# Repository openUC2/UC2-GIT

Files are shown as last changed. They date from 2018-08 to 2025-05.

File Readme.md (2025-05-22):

<p align="left">
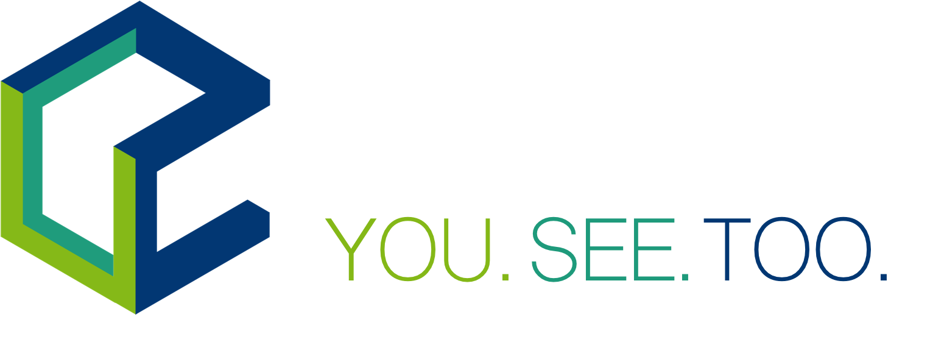
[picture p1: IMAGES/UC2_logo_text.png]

</p>

# **UC2 - Open and Modular Optical Toolbox**

**⚠️ IMPORTANT NOTICE:**
This repository is no longer actively maintained. But don’t worry—**openUC2 is more alive than ever!**
For the latest updates, documentation, and community discussions, please check out the following resources:

* 💬 **Forum**: [openuc2.discourse.group](https://openuc2.discourse.group)
* 📚 **Wiki**: [openuc2.github.io](https://openuc2.github.io)
* 🔧 **Firmware**: [youseetoo.github.io](https://youseetoo.github.io)
* 🌐 **Website**: [openuc2.com](https://openuc2.com)

**Open-source forever** – so we can become the *Raspberry Pi for optics!*

---

**New**: :mag_right: A [youtube seminar](https://www.youtube.com/watch?v=Jp5TOqvf7Nc&ab_channel=mitirtmfm) that describes UC2:  :mag:

**New**: :mag_right: The MiniBOX insert can be produced with a laser cutter now! Also, we improved the page and added some tips and trick for working with the [MiniBOX](./TheBOX/SimpleBOX)! Build it, use it, share your thoughts! :mag:

**New**: We got the official open hardware certification of OSHWA, under [`[OSHW] DE00110 | Certified open source hardware | oshwa.org/cert`](https://certification.oshwa.org/de000110.html)!

**New**: :boom: **UC2_v3 is now released!** :boom: [Watch how much time the IM cubes can save!](https://www.youtube.com/watch?v=M_oqieogAOo&feature=youtu.be&ab_channel=openUC2)   
*We are working on making the IM Cubes and Puzzles available for sale, but we are not able to offer a 'BUY' button yet. If you are interested in buying some components, contact us via email info@useetoo.org*

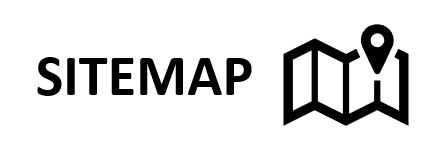
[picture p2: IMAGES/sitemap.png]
[](./SITEMAP.md)

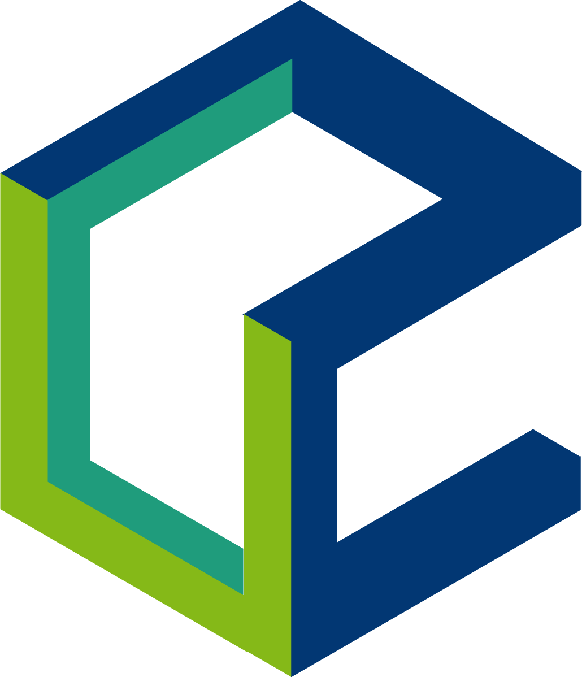
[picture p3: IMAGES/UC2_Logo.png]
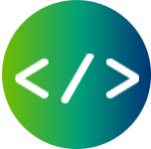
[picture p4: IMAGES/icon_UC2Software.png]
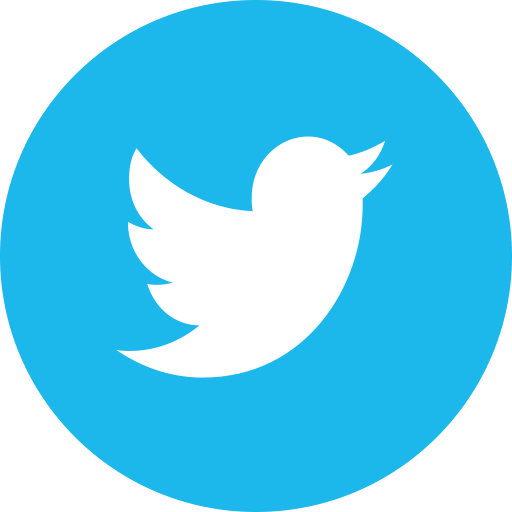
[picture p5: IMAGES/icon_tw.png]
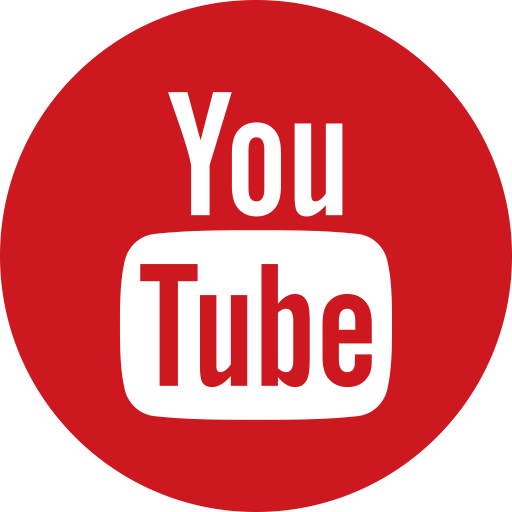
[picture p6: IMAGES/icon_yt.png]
[](https://www.useetoo.org) [](https://github.com/bionanoimaging/UC2-GIT) [](https://github.com/bionanoimaging/UC2-Software-GIT) [](https://twitter.com/openuc2)  [](https://www.youtube.com/channel/UCcHFzXTdC1Ro0OMnHS_54UA) 

Cite this repository: 

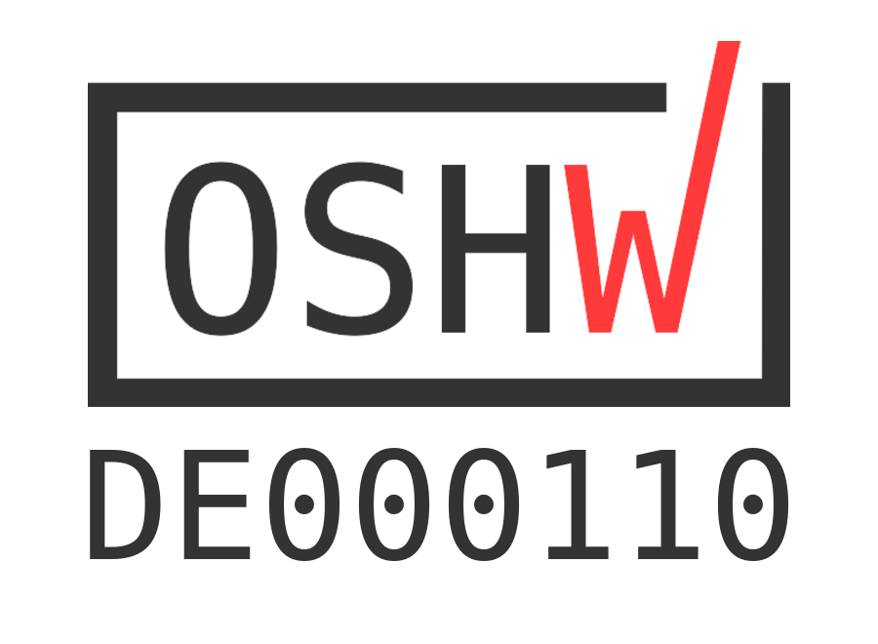
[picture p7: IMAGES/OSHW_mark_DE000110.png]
[](https://certification.oshwa.org/de000110.html)
This project provides certified open hardware.

---

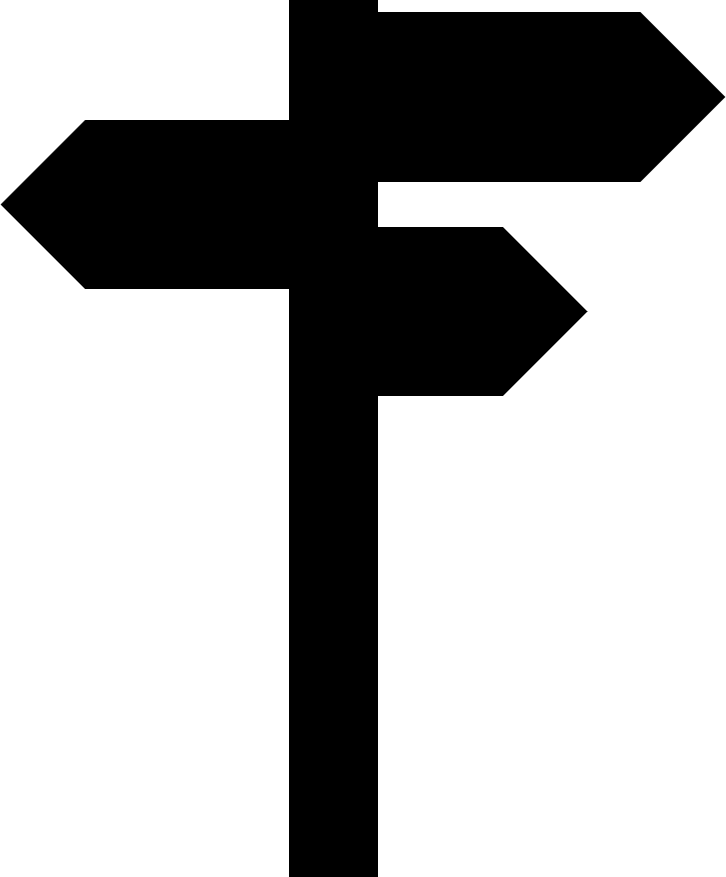
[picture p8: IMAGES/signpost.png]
#  Start here! Everything is open-source - simply join!

## Steps to reproduce and use the toolbox:
<p align="center">
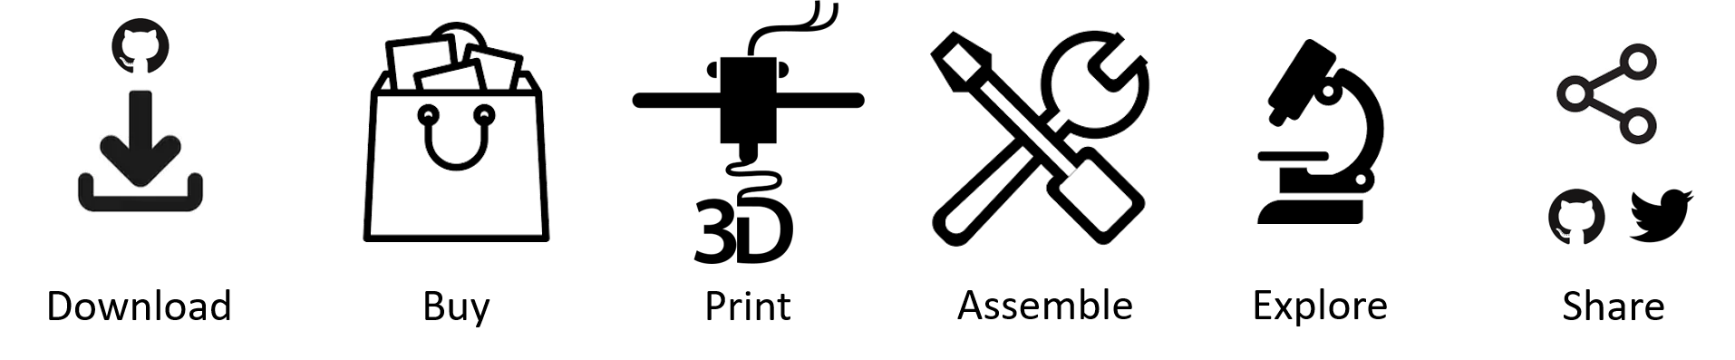
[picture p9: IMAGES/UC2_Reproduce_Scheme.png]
 
</p>

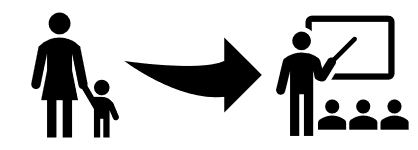
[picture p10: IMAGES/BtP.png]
## Too many new things? Follow our tutorials [ From a Beginner to a Professional](./TUTORIALS)!

## Already familiar? Click here if you are looking for...
TheBOX | General toolbox  | Specific setup |Workshops
:------:|:------:|:------:|:------:
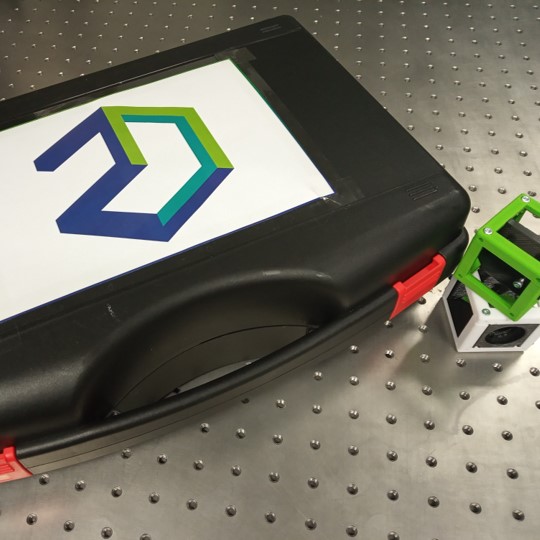
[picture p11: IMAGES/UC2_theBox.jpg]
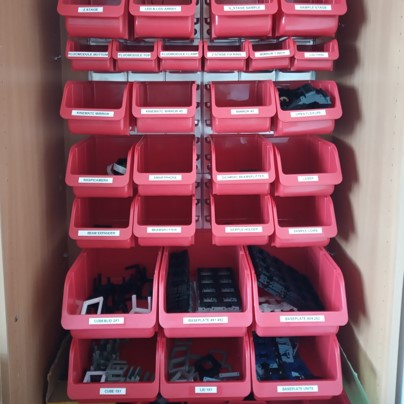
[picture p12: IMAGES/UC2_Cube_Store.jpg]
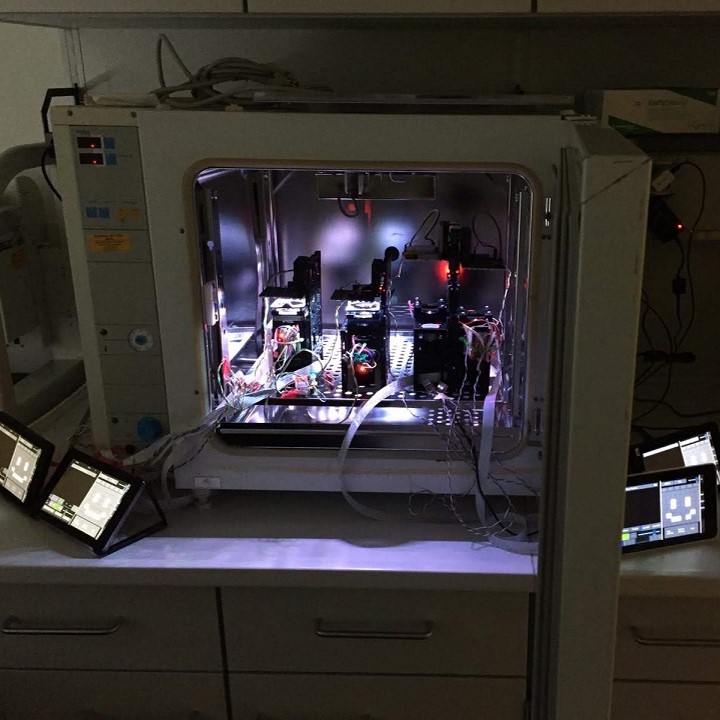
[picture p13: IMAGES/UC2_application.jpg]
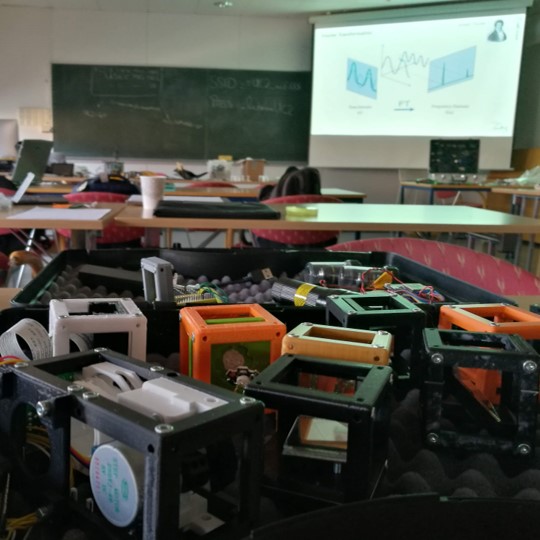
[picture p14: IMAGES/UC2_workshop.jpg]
[](./TheBOX)|[](./CAD)|[](./APPLICATIONS)|[](./WORKSHOP)
[Choose a version and build your own BOX.](./TheBOX) | [Explore the toolbox and its applications.](./CAD) | [Alternatives for many Microscopy methods... and more.](./APPLICATIONS) | [Host or join a UC2 workshop.](./WORKSHOP)

## [Get Involved! Contribute to the project!](CONTRIBUTING.md)

## ... or keep on reading to learn more!

---

## Making **open-science** great again!

**WARNING THIS SIDE IS UNDER REVISION! MANY CHANGES AHEAD!**

**UC2** is a general-purpose modular framework for making interactive (electro)-optical projects. Most optical systems such as microscopes follow a simple **4f** or Fourier-optical principle, where lenses are aligned such that focal-planes of adjacent components overlap to limit the amount of aberrations as much as possible and to be able to predict the system-behavior easily using Fourier-transforms.

<p align="center">
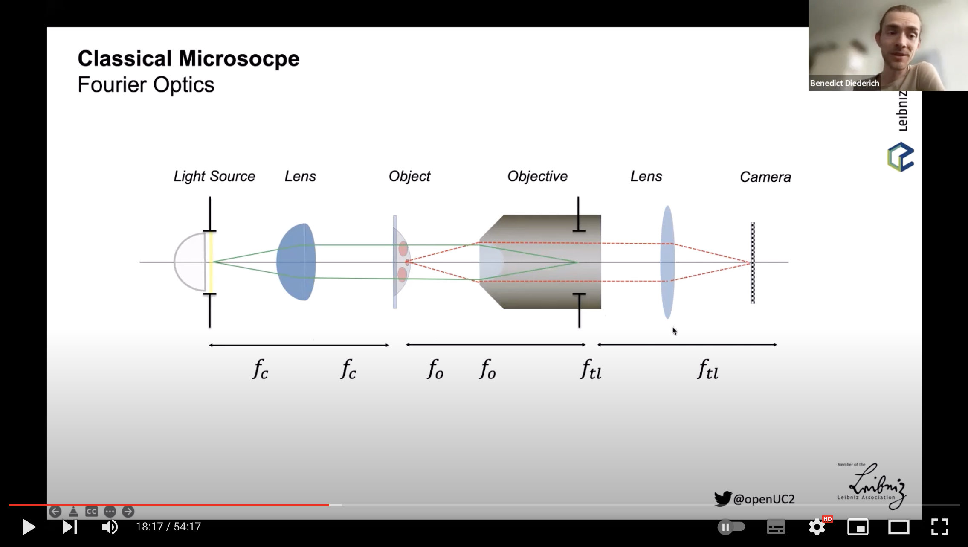
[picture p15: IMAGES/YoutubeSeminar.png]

<br> A recent seminar explaining the core concept of UC2 and their recent advances <br>
<p>

Following this idea, a microscope as shown in **Fig 1** creates an angular magnification depending on the focal lenghts of the objective f<sub>obj</sub> and tube lens f<sub>tube</sub>:

***M<sub>4f</sub>=  f<sub>tube</sub>/f<sub>obj</sub>***

<p align="center">
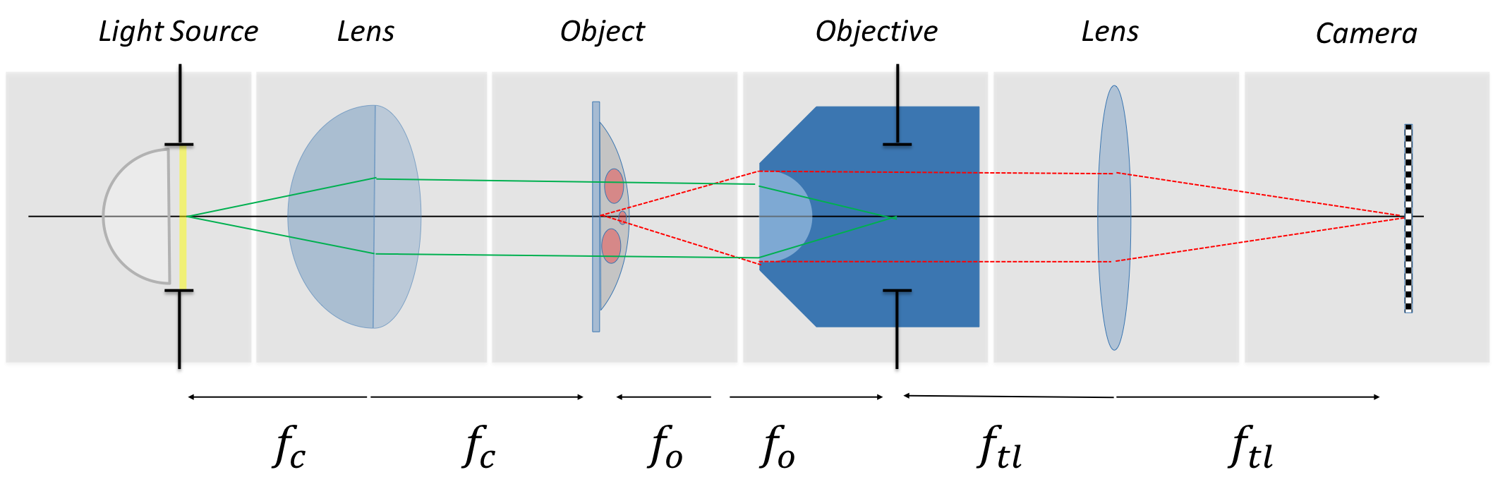
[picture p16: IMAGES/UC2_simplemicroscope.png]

<br> Fig. 1: Fourier-Optical Setup; Koehler Illumination where the illumination plane is conjugate to the objective pupil plane (BFP)
</p>

Besides optical components, the **UC2** building blocks can also host electronics such as **Arduinos** or **ESP32s** to create ''smart'' functions like LED array illumination, Z-stages, et cetera. Communication can be granted through the wired **USB Serial** BUS or the wireless **REST-API**. For this the dedicated [**UC2-REST**](https://github.com/openUC2/UC2-REST/blob/master/README.md) will help you setting everything up.

**UC2** is in active development. It is meant to be used not only by beginners, but also for professionals dealing with optical setups on a daily basis. Its magnetic click-and-go concept simplifies the process of aligning and adjusting the parts giving new tools acting as rapid-prototyping devices. It also comes with a series of open-source workshops (in the future) explaining the theory behind optics.

People are also encouraged to share their work. We are curious what the community is doing with our little blocks. All necessary details to modify the design of the blocks are given in the sub-folders of the specific folders. Share your ideas through our [@openUC2-Twitter account](https://twitter.com/openuc2).

With the version *UC2_v3* we introduced an **injection moulded (IM) cube**. This makes the assembly easier becuase no screws or magnets are needed for the Base Cube. But there is also a **3D-printed (3DP) cube** that is alternative to the IM one an it is fully compatible - the cubes and baseplates can be arbitrarily combined.   
Find out more about the two different Cube designs in [ASSEMBLY_CUBE_Base](./CAD/ASSEMBLY_CUBE_Base) and more about the baseplate puzzles in [ASSEMBLY_Baseplate](./CAD/ASSEMBLY_Baseplate).

*We are working on making the IM Cubes and Puzzles available for sale, but we are not able to offer a 'BUY' button yet. If you are interested in buying some components, contact us via email info@useetoo.org*

A full cube + base-plate looks like that:
<p align="center">
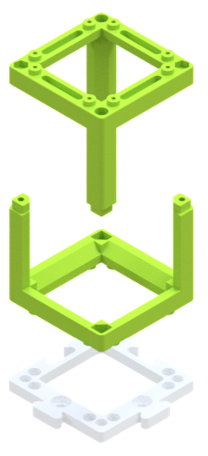
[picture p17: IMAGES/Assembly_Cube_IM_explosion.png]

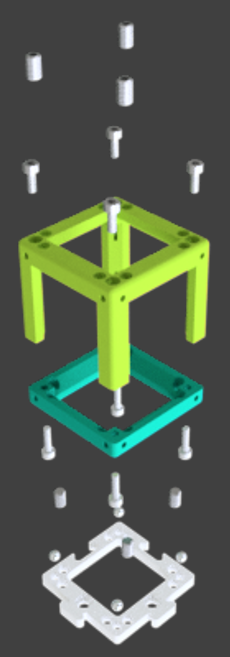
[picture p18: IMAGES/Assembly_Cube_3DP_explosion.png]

<br> Fig. 2: Assembly of the cube + base-plate; <br>
LEFT: IM Cube - Two identical halves of the Cube are pressed together, the Cube connects to the baseplate via lego-like pins; <br>
RIGHT: 3DP Cube - A set of ferro-magnetic screws hold the lid and base-cube in place and connect to four 5mm Neodym ballmagnets sitting in the baseplate, and extra set of M5 screws further fixes the cube to the baseplate and supports the alignment; Optical components find their place inside the cube.
</p>

:grey_exclamation: If you are still working with the v2 version of the cube, you find the documentation in the [UC2_v2 branch](https://github.com/bionanoimaging/UC2-GIT/tree/UC2_v2). Check out the Modular Developer Kit to learn about the [UC2 version history](./MDK#uc2-version-history).

**UC2** can be used with cameras from the Raspberry Pi world, but creates even more beautiful images with your cellphone. Thus making cutting edge-research not only affordable, but also available.
A more in-detail project description can be found in the [UC2 White-Paper](./TUTORIALS/DOCUMENTS/UC2_Whitepaper.pdf)

## UC2 as an "open-standard"

The idea is to use **UC2** as an open-standard or bridge to external hardware components and devices such as cameras or lenses. An already existing or customized adapter/insert creates the link to the **UC2** eco-system. A variety of ready-to-use adapters can be found in the folder [CAD](./CAD).

<p align="center">
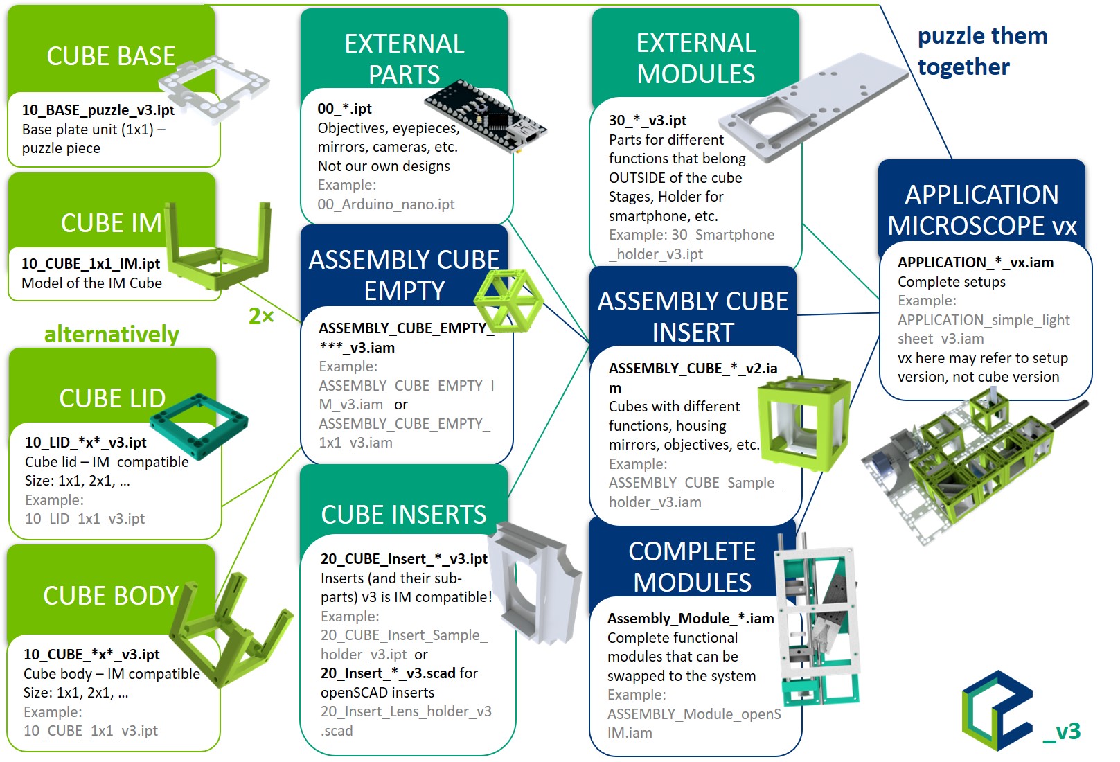
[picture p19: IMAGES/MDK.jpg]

<br> Fig. 3: The structure of any UC2 assembly follows the green lines; A basic cube can hold an insert thus adapting to different components (i.e. lenses, etc.); A number of assembled cube-modules can form a complex optical system here called application
</p>

A more in-detail description of the **MDK** (**M**odular **D**eveloper **K**it) which explains how ***your idea*** can be adapted to the module system can be found in the [MDK](./MDK)-folder. There you also found an explanation about the UC2 version history, if you found some confusing information through the repository.

If you have a new part, we are eager to see it. Please feel free to share it on available websites like Twitter, Thingiverse, Github or any other platform of choice!

### Read more about the project in our papers:
The UC2 paper: A versatile and customizable low-cost 3D-printed open standard for microscopic imaging is available on [Nature Communications](https://www.nature.com/articles/s41467-020-19447-9) 
All data from the paper is available in [Zenodo](https://doi.org/10.5281/zenodo.4018965)   
The Pre-print of the SIM+ISM paper is available on [Biorxiv](https://www.biorxiv.org/content/10.1101/2021.01.08.425840v1)    
The COSI conference paper is out on [OSA](https://www.osapublishing.org/abstract.cfm?uri=ISA-2019-ITh3B.5)  

Where next? [](./SITEMAP.md)

### Complete overview of setups, modules, parts to buy and parts to print
I'm afraid we outgrew the situation where we could provide a real complete overview. If you're looking for something specific, check the [SITEMAP](./SITEMAP.md) of the core repository and the [overview of the openUC2 repositories](./REPO_OVERVIEW.md).

For the basic modules and setups, find a complete shopping'n'printing list including estimated prices for all modules and setups in this [BILL OF MATERIALS](https://docs.google.com/spreadsheets/d/1U1MndGKRCs0LKE5W8VGreCv9DJbQVQv7O6kgLlB6ZmE/edit?usp=sharing)!

### List of available Setups

Our goal is to make as many setups as possible available, so that people can play with it. Basically everything's possible, you just need to think in blocks! Please have a look in the [APPLICATIONS](./APPLICATIONS/Readme.md) folder for the up to date list of the setups.

<p align="center">
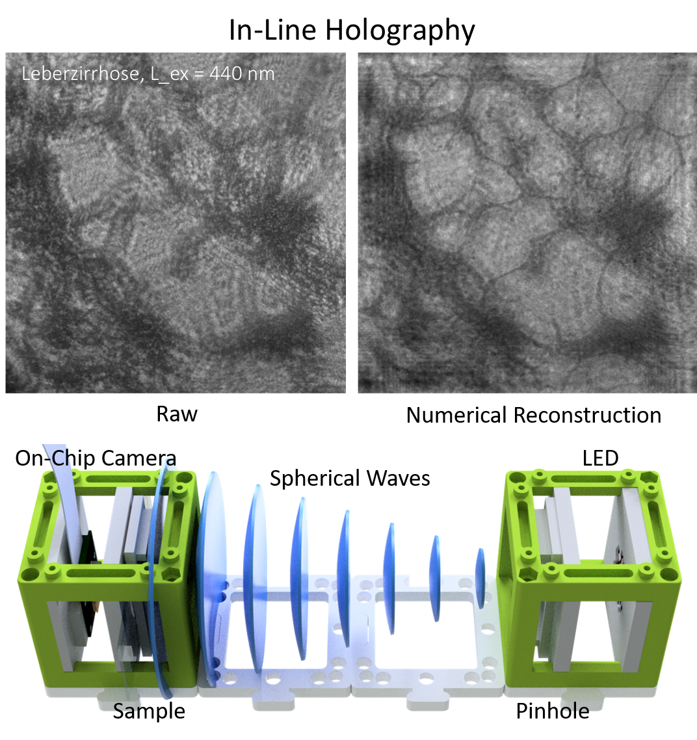
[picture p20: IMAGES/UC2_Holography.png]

<br> Fig. 4: In-line holographic microscope
</p>

### Repositories

Currently, **UC2** consists of the following repositories:

* [UC2 Hardware Repo (core)](https://github.com/openUC2/UC2-GIT) (this repository) - [SITEMAP](./SITEMAP.md)
* [UC2-REST Repo](https://github.com/openUC2/UC2-REST) - firmware for microcontrollers
* [UC2 ImSwitch](https://github.com/beniroquai/ImSwitch) - control software for microscopes
* A whole bunch of other repositories! In order to keep the main repository small and maintain a good structure, each sub-project has its own repository - find the [overview here](./REPO_OVERVIEW.md)

### Software

There is a GitHub repository dedicated for the UC2 software. It can be found in the [UC2-REST Repo](https://github.com/openUC2/UC2-REST). 

The old and deprecated Raspi version can be found [here](https://github.com/bionanoimaging/UC2-Software-GIT). This supports you with controller APPS for the Raspberry Pi and Android Cellphones.

### Workshops

The documented workshops can be found in the folder [WORKSHOP](./WORKSHOP) and give a step-by-step introduction into the system. We have done multiple workshops together with the HHMI Janelia Farm, UiO Oslo, Lichtwerkstatt Jena and Leibniz IPHT Jena e.V.  
If you're interested we are happy to host one near you!

## Get Involved

This project is open so that anyone can get involved. You don't even have to learn CAD designing or programming. Find ways you can contribute in  [CONTRIBUTING](CONTRIBUTING.md)

## Kits, License and Collaboration

<p >

</p>

This project is open-source and is released under the CERN open hardware license. Our aim is to make the kits commercially available.
We encourage everyone who is using our Toolbox to share their results and ideas, so that the Toolbox keeps improving. It should serve as a easy-to-use and easy-to-access general purpose building block solution for the area of STEAM education. All the design files are generally for free, but we would like to hear from you how is it going.

You're free to fork the project and enhance it. If you have any suggestions to improve it or add any additional functions make a pull-request or file an issue.

Please find the type of licenses [here](./License.md)

REMARK: All files have been designed using Autodesk Inventor 2019 (EDUCATION)

## Showcase

This is the mess you can end up during Fourier-optics session using UC2 components. Pure-fun! :-)

<p align="center">

</p>

## Credits
If you find this project useful, please like this repository, follow us on Twitter and cite the webpage! :-)

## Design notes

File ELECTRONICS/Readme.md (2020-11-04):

#  Electronics
 Here you'll find the schematics for the wiring of the UC2 parts.

* For printing and assembly of all the cubes and modules go to [CAD](../CAD)
* For complete setups go to [APPLICATIONS](../APPLICATIONS)
* For setups compilations go to [TheBOX](../TheBOX)
* For beginner's tutorials, how-to guides and more guidelines go to [TUTORIALS](../TUTORIALS)
* For information on the software go to the dedicated repository [UC2-Software-GIT](https://github.com/bionanoimaging/UC2-Software-GIT)
* For the Bill of Materials go to [RESOURCES](../TUTORIALS/RESOURCES)
* For anything else, have a look at the [SITEMAP](../SITEMAP.md)

---
# If all the wiring scares you, [click here ](./ELECTRONICS_FOR_DUMMIES)
---

Most connections can be established with pin-connection (male/female), as you see in the [simplified tutorial](./ELECTRONICS_FOR_DUMMIES). For durable connection, please solder everything! You're not expected to have perfect soldering skills though. Have a look in the [TUTORIALS](../TUTORIALS) for some soldering guidelines. Be careful not to mix up +/-, otherwise you might cause shortcuts which would very likely fry the Pi or the Arduinos/ESP32s.

## Available schemes and guidelines
* [Z-stage and Sample-Stage](./Z-Stage)
* [LED matrix](./LED-Matrix)
* [Fluo-LED for Z-stage](./FLUO-LED)
* [XY-Stage](./XY-Stage)
* [Raspberry Pi](./RASPBERRY-PI)
* [Magnetic connectors (v0)](./Magnetic-Connectors)

    This section needs an update!

## Wire Diagrams/Schematics
All schemes are put together with the Open-Source Software [Fritzing](http://fritzing.org/).

## General Wiring (Arduino Nano; I2C)
For the I2C Bus we use a 4-wire colour-code as follows:

- **5V** - White
- **GND** - Yellow
- **Data** - Green
- **CLK** - Brown

The junctions are connected with [WaGo Snapping Clamps, Compact Wago 2273-203 -> Amazon](https://www.amazon.de/Wago-VERBINDUNGSKLEMME-3POL-2273-203/dp/B075ZRQCGZ):
<p align="center">
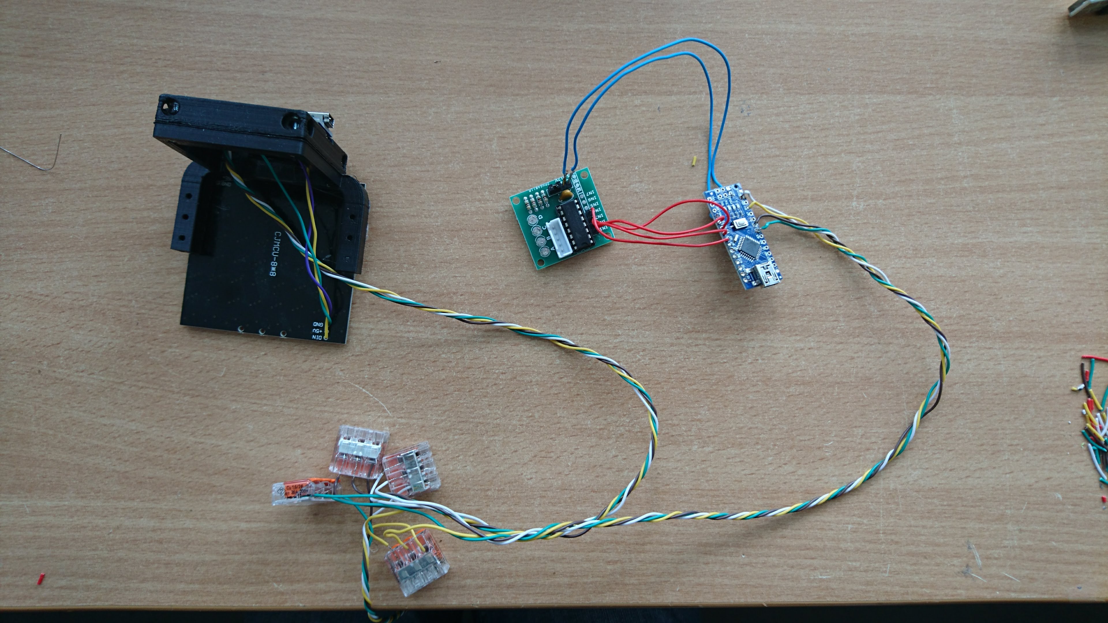
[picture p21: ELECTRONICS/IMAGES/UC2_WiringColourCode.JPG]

</p>

# Done with the wiring? Then it's time for [software](https://github.com/bionanoimaging/UC2-Software-GIT)!

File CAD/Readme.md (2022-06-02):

## CAD Files
 Here you can find the necessary .stl parts for the different modules (cubes) and setups ([APPs](../APPLICATIONS)).

* For complete setups go to [APPLICATIONS](../APPLICATIONS)
* For setups compilations go to [TheBOX](../TheBOX)
* For beginner's tutorials, how-to guides and more guidelines go to [TUTORIALS](../TUTORIALS)
* For information on the electronic parts go to [ELECTRONICS](../ELECTRONICS)
* For information on the software go to the dedicated repository [UC2-Software-GIT](https://github.com/bionanoimaging/UC2-Software-GIT)
* For the Bill of Materials go to [RESOURCES](../TUTORIALS/RESOURCES)
* For anything else, have a look at the [SITEMAP](../SITEMAP.md)

This is a growing list of available modules coming along with tutorials and assembly instructions. The most important part is the core building block as you find in every modular toolbox. A detailed description of the **UC2** cube can be found [here](./ASSEMBLY_CUBE_Base_v2/Readme.md).

## General Naming Convention and Structure of UC2

<p align=center>

</p>

## UC2 version history
When you search through the repository, you find that not all the images show the same cubes and baseplates. This is due to the evolution of the basic building blocks. In order to help you not to get lost, in the [Modular Developer Kit](../MDK#uc2-version-history) is a short explanation of how the cubes evolved.

#### v3 = 3D-printed AND Injection Moulded (*November 2020*)
This is the current version. The cube comes in two versions that are fully compatible with each other. You can either print all the baseplates and cubes and assemble and connect them using screws and magnets, or you can use the IM cubes and baseplate puzzles that connect via the lego-like pins.

The IM cube is shown on the left, the 3DP (3D-printed) cube is on the right. Find the details about the base cube in [ASSEMBLY_CUBE_Base](./ASSEMBLY_CUBE_Base).
<p align=center>
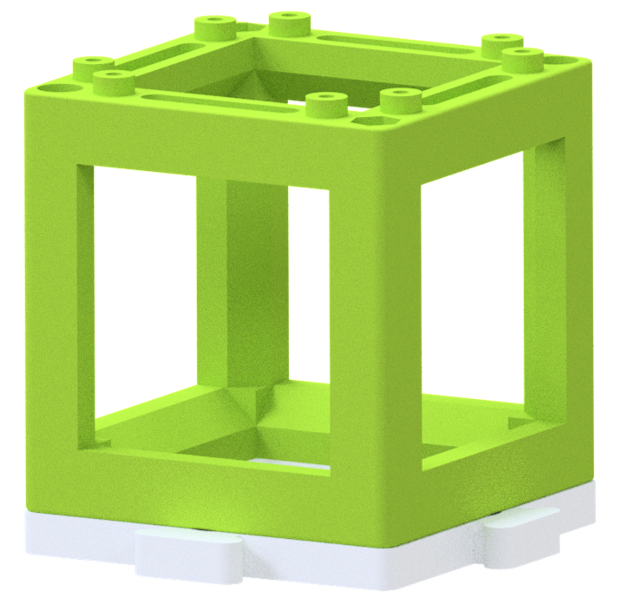
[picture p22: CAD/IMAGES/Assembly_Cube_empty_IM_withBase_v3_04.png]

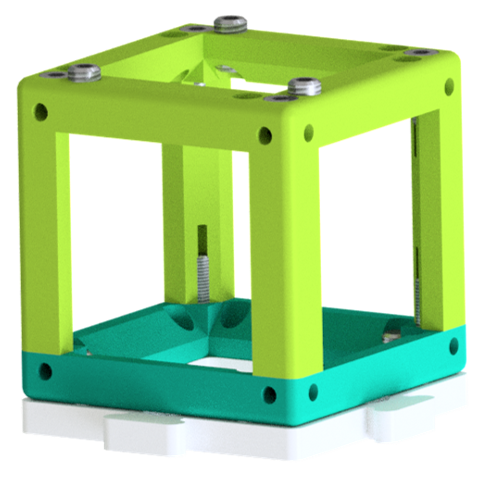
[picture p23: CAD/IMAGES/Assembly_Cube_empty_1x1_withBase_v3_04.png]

</p>

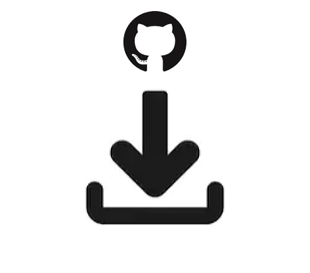
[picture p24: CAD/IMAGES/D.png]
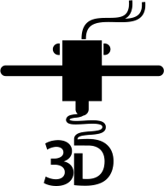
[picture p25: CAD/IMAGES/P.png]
##  Printing
The .stl files of the respective modules can be downloaded and printed. Have a look at our [TUTORIALS](../TUTORIALS) section for some introductory information regarding 3D printing, shopping for components and more.

## List of available Modules (CUBEs):
Each folder contains a step-by-step tutorial which describes how the module has to be assembled.

Link             |  Image of the part
:-------------------------:|:-------------------------:
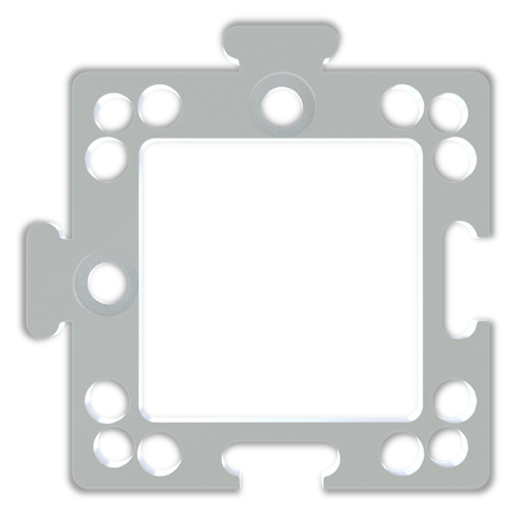
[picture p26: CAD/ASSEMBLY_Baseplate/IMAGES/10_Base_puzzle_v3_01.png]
[Base Plate puzzle](./ASSEMBLY_Baseplate)  |  [](./ASSEMBLY_Baseplate)
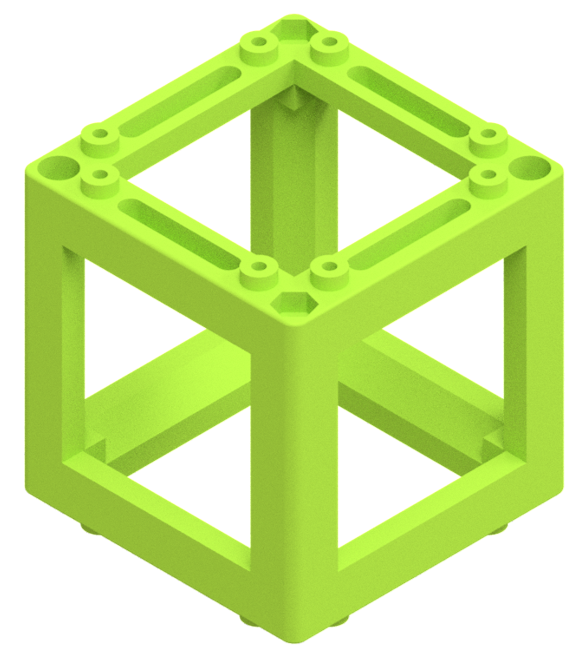
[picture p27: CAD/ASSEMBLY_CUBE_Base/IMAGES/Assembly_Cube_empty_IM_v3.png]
[CUBE Base](./ASSEMBLY_CUBE_Base)  |  [](./ASSEMBLY_CUBE_Base)
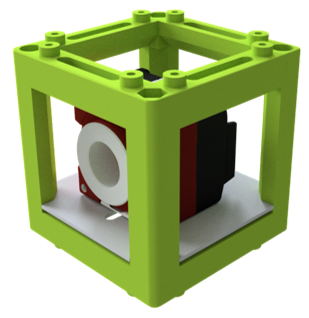
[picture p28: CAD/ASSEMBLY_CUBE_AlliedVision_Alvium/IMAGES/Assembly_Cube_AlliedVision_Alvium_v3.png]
[Allied Vision Cam](./ASSEMBLY_CUBE_AlliedVision_Alvium) | [](./ASSEMBLY_CUBE_AlliedVision_Alvium)
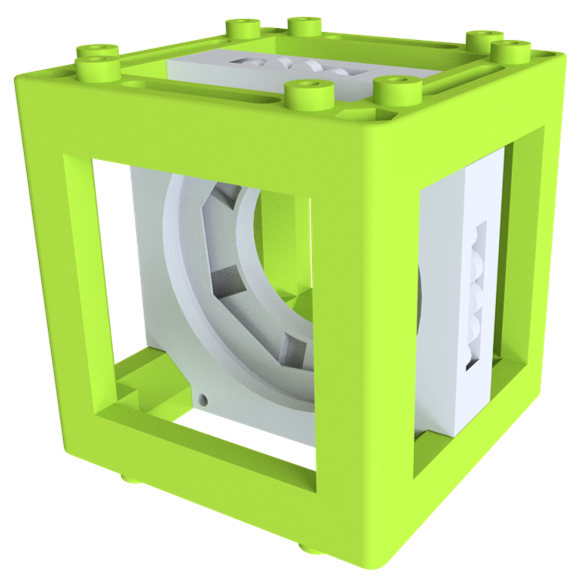
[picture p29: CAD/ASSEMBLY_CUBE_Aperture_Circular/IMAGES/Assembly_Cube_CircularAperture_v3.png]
[Circular Aperture](./ASSEMBLY_CUBE_Aperture_Circular)  |  [](./ASSEMBLY_CUBE_Aperture_Circular)
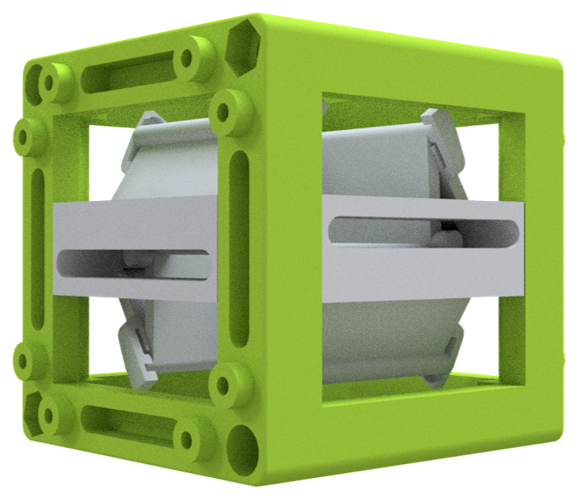
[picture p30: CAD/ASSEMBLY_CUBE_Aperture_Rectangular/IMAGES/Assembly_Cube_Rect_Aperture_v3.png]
[Rectangular Aperture](./ASSEMBLY_CUBE_Aperture_Rectangular)  |  [](./ASSEMBLY_CUBE_Aperture_Rectangular)
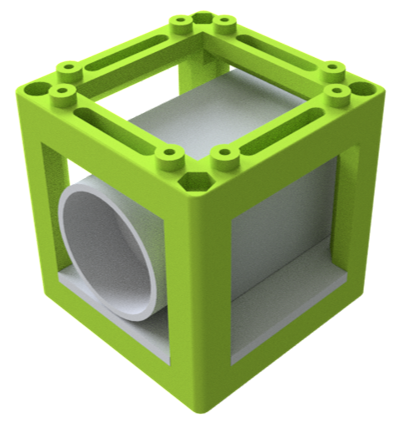
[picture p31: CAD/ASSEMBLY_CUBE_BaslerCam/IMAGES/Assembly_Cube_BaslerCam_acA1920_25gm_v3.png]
[Basler Cam](./ASSEMBLY_CUBE_BaslerCam) | [](./ASSEMBLY_CUBE_BaslerCam)
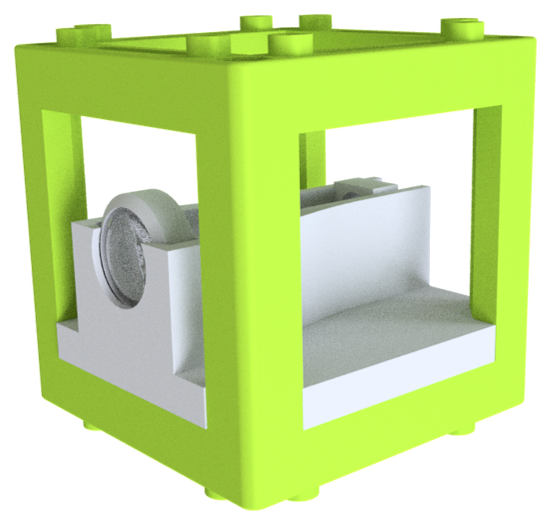
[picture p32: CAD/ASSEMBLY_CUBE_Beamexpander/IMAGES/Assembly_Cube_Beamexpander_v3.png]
[Beam Expander](./ASSEMBLY_CUBE_Beamexpander)  |  [](./ASSEMBLY_CUBE_Beamexpander)
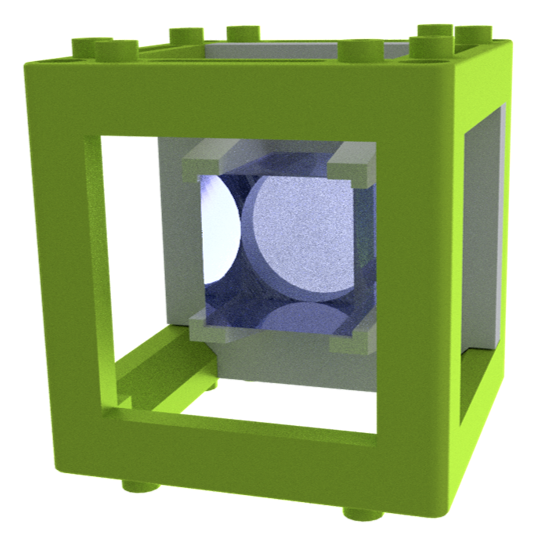
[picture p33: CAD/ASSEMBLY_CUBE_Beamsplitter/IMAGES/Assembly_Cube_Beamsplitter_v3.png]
[Beam splitter](./ASSEMBLY_CUBE_Beamsplitter)  |  [](./ASSEMBLY_CUBE_Beamsplitter)
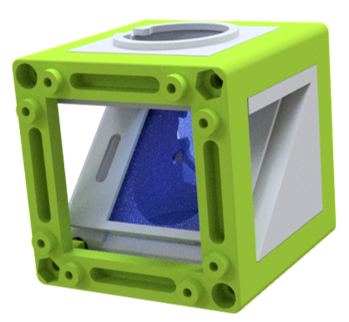
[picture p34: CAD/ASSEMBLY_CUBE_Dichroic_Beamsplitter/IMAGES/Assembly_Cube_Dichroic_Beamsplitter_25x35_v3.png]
[Dichroic Beam splitter](./ASSEMBLY_CUBE_Dichroic_Beamsplitter) | [](./ASSEMBLY_CUBE_Dichroic_Beamsplitter)
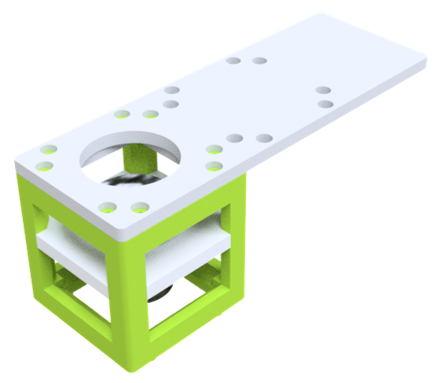
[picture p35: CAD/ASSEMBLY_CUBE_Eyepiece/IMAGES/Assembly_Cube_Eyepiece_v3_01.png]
[Eyepiece + Smartphone](./ASSEMBLY_CUBE_Eyepiece) | [](./ASSEMBLY_CUBE_Eyepiece)
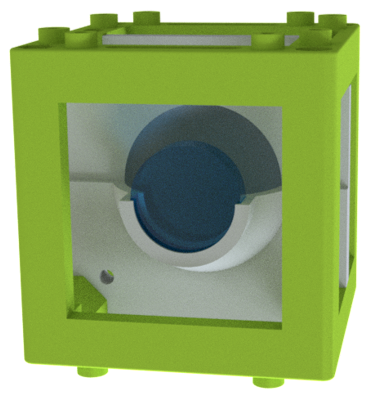
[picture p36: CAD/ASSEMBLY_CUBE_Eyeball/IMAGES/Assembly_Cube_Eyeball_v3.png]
[Eyeball Cube ](./ASSEMBLY_CUBE_Eyeball) | [](./ASSEMBLY_CUBE_Eyeball)
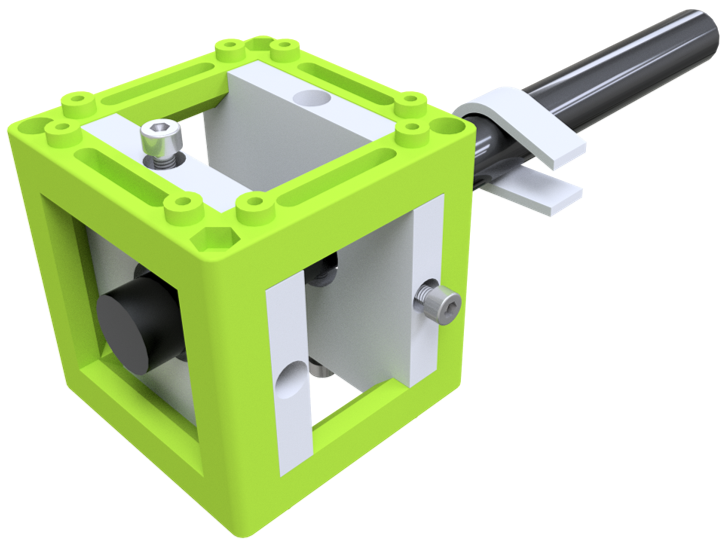
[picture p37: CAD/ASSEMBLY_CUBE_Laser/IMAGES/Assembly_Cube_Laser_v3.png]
[Laser](./ASSEMBLY_CUBE_Laser) | [](./ASSEMBLY_CUBE_Laser)
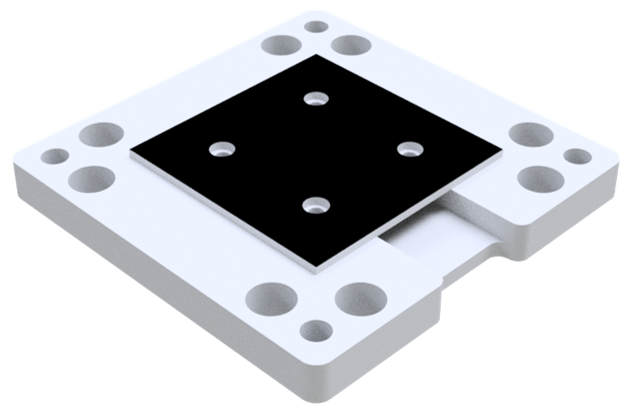
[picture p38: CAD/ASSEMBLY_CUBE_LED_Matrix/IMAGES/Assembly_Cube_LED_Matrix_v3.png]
[LED Matrix](./ASSEMBLY_CUBE_LED_Matrix) | [](./ASSEMBLY_CUBE_LED_Matrix)
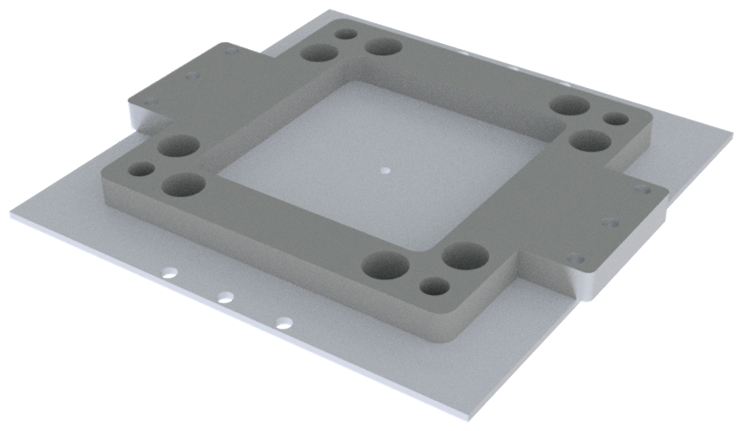
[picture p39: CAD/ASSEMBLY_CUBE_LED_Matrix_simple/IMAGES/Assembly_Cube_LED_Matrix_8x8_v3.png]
[LED Matrix (simple)](./ASSEMBLY_CUBE_LED_Matrix_simple) | [](./ASSEMBLY_CUBE_LED_Matrix_simple)
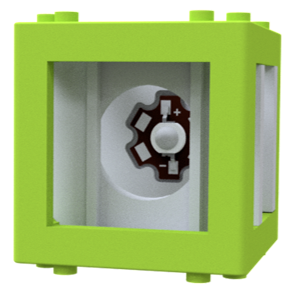
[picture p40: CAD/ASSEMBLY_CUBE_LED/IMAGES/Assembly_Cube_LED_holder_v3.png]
[LED Star](./ASSEMBLY_CUBE_LED) | [](./ASSEMBLY_CUBE_LED)
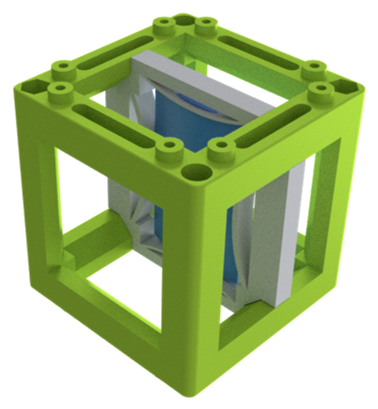
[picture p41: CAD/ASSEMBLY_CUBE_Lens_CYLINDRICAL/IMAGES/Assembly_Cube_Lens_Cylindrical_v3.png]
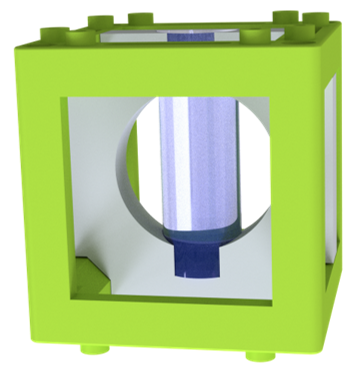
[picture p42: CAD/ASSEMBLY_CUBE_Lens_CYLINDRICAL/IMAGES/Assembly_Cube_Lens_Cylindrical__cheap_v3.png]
[Lens (cylindrical)](./ASSEMBLY_CUBE_Lens_CYLINDRICAL) | [](./ASSEMBLY_CUBE_Lens_CYLINDRICAL)
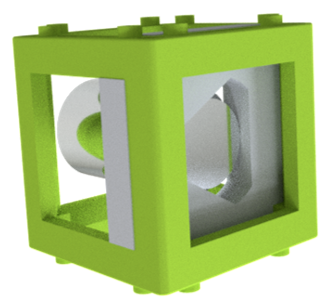
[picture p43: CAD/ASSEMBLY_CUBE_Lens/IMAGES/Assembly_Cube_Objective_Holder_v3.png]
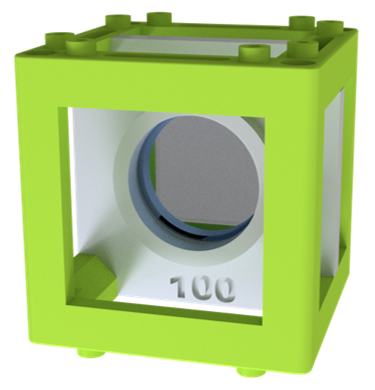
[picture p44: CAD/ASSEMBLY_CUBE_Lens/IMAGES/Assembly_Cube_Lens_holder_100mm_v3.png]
[Lens (standard)](./ASSEMBLY_CUBE_Lens) | [](./ASSEMBLY_CUBE_Lens)
[Mirror (45°)](./ASSEMBLY_CUBE_Mirror_45) | [](./ASSEMBLY_CUBE_Mirror_45) [](./ASSEMBLY_CUBE_Mirror_45)
[Mirror, kinematic (45°)](./ASSEMBLY_CUBE_Mirror_Kinematic_45) | [](./ASSEMBLY_CUBE_Mirror_Kinematic_45)
[Mirror, kinematic (0°)](./ASSEMBLY_CUBE_Mirror_Kinematic) | [](./ASSEMBLY_CUBE_Mirror_Kinematic)
[Raspi Cam](./ASSEMBLY_CUBE_RaspiCam) | [](./ASSEMBLY_CUBE_RaspiCam)
[S-Stage v2.1](./ASSEMBLY_CUBE_S-STAGE_v2.1) | [](./ASSEMBLY_CUBE_S-STAGE_v2.1)
[Sample Holder Cube](./ASSEMBLY_CUBE_Sample_Holder) | [](./ASSEMBLY_CUBE_Sample_Holder)
[Magnetic Sample Holder](./ASSEMBLY_CUBE_Sample_Holder) | [](./ASSEMBLY_CUBE_Sample_Holder)
[Sample Holder Comb](./ASSEMBLY_CUBE_Sample_Holder) | [](./ASSEMBLY_CUBE_Sample_Holder)
[Thorlabs Adapter](./ASSEMBLY_CUBE_Thorlabs) | [](./ASSEMBLY_CUBE_Thorlabs)
[Z-Stage (Objective) mechanical](./ASSEMBLY_CUBE_Z-STAGE_mechanical) | [](./ASSEMBLY_CUBE_Z-STAGE_mechanical)
[Z-Stage (Sample) v3](./ASSEMBLY_CUBE_Z-STAGE_sample) | [](./ASSEMBLY_CUBE_Z-STAGE_sample)
[XYZ-Stage v0](./ASSEMBLY_XYZ-STAGE_v0) | [](./ASSEMBLY_XYZ-STAGE_v0)
[ASSEMBLY_CUBE_ArduCamUSB](./ASSEMBLY_CUBE_ArduCamUSB) | [](./ASSEMBLY_CUBE_ArduCamUSB)

## More external modules 
Link             |  Image of the part
:-------------------------:|:-------------------------:
[Optics rotator (e.g. Diffuser, Polarizer)](https://github.com/openUC2/UC2-Motorized-Rotator) | [](https://github.com/openUC2/UC2-Motorized-Rotator)
[Microsyringepump](https://github.com/openUC2/UC2-MicroSyringePump) | [](https://github.com/openUC2/UC2-MicroSyringePump)
[Multicolour Module](https://github.com/openUC2/UC2-MultiColour) | [](https://github.com/openUC2/UC2-MultiColour)
[Waveguide Coupling Module](https://github.com/openUC2/UC2-waveguiding) | [](https://github.com/openUC2/UC2-waveguiding)
[Motorized XY table](https://github.com/openUC2/UC2-Motorized-XY-Table) | [](https://github.com/openUC2/UC2-Motorized-XY-Table)
[Micromanipulator Module](https://github.com/openUC2/openCM2_hardware) | [](https://github.com/openUC2/openCM2_hardware)
[Motorized XY micrometer stage](https://github.com/openUC2/UC2-MicronStage) | [](https://github.com/openUC2/UC2-MicronStage)

## List of available Supplements:
* [ELECTRONICS-RaspiTFT-Case](./EXT_ELECTRONICS-RaspiTFT-Case)
* [ELECTRONICS-Mount](./EXT_ELECTRONICS-Mount)
* [Alignment tool](./EXT_Alignment_Tool)
* [Adapter to openflexure stage](./CUBE_INSERT_OpenFlexure_Deltastage)

##  List of available [Applications (APPs)](../APPLICATIONS)

### Complete overview of setups, modules, parts to buy and parts to print
Find a complete shopping'n'printing list including estimated prices for all modules and setups in this [GoogleDrive Spreadsheet](https://docs.google.com/spreadsheets/d/1U1MndGKRCs0LKE5W8VGreCv9DJbQVQv7O6kgLlB6ZmE/edit?usp=sharing)!

##  Participate
If you have a cool idea, please don't hesitate to contact us, we are happy to incorporate it in our design to make it even better.  
More setups are coming soon!
Inspire us with your ideas - we try to make it work! :-)

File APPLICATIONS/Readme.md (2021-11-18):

## Applications
 Here you can find all the optical setups we tested or proposed so far.

* For printing and assembly of all the cubes and modules go to [CAD](../CAD)
* For setups compilations go to [TheBOX](../TheBOX)
* For beginner's tutorials, how-to guides and more guidelines go to [TUTORIALS](../TUTORIALS)
* For information on the electronic parts go to [ELECTRONICS](../ELECTRONICS)
* For information on the software go to the dedicated repository [UC2-Software-GIT](https://github.com/bionanoimaging/UC2-Software-GIT)
* For the Bill of Materials go to [RESOURCES](../TUTORIALS/RESOURCES)
* For anything else, have a look at the [SITEMAP](../SITEMAP.md)

This is a growing list of available optical setups coming along with tutorials and alignment instructions. The most important part is the core building block as you find in every modular toolbox. A detailed description of the the **UC2** cube can be found [here](../CAD/ASSEMBLY_CUBE_Base_v2/Readme.md).

##  List of available Applications (APPs)

### Compilations

* [TheBOX: Concept of a ready-to-use box containing multiple setups at once](../TheBOX/)
* [SimpleBOX: Optical setups from elementary to high-school level ](../TheBOX/SimpleBOX)
* [FullBOX: Optical setups from high-school to university level (contains electronics)](../TheBOX/FullBOX)
* [CourseBOX: Optical setups for Optics and Microscopy courses](../TheBOX/CourseBOX)
* [PolarBOX : Optical setups for the polarization of light ](../TheBOX/PolarBOX)

### SIMPLE Setups
* [SIMPLE - Projector](./APP_SIMPLE-Projector)
* [SIMPLE - Telescope](./APP_SIMPLE-Telescope)
* [SIMPLE - Smartphone Microscope](./APP_SIMPLE-Smartphone_Microscope)

### BASIC Setups
* [In-Incubator Microscope with X/Y/Z-control and adaptive illumination](./APP_Incubator_Microscope)
* [Light sheet Microscope](./APP_LIGHTSHEET_Workshop)
* [In-line Holographic Microscope](./APP_INLINE_HOLOGRAM)
* [Abbe Diffraction Experiment](./APP_Abbe_Setup)
* [Michelson Interferometer (Interference effect of light)](./APP_Michelson_Interferometer)
* [Mach-Zehnder Interferometer (Interference effect of light)](./APP_Mach-Zehnder_Interferometer)
* [Double Slit Experiment (Interference effect of light)](./APP_Double-slit_Experiment)
* [Spectrometer](APP_Spectrometer)

### POLARIZATION Setups
* [Crossed Polarizers](APP_POL_Crossed_Polarizers)
* [Three Polarizers](APP_POL_Three_Polarizers)
* [Circular Polarizer](APP_POL_Circular_Polarizer)
* [Optically Active Solution Experiment](APP_POL_Polarization_using_optically_active_solution)
* [Brewster's Angle Experiment](APP_POL_Brewster_Angle_Experiment)
* [Stress Birefringence](APP_POL_Stress_Birefringence)
* [Many Microscope Slides Experiment](APP_POL_Many_Microscope_Slides_Experiment)
* [Newton's Rings Experiment](APP_POL_Newtons_Rings_Experiment)

### COMPLEX Setups and sub-projects
All the more complicated systems have their own repository - see the overview [here](../REPO_OVERVIEW.md).

## General Naming Convention and Structure of UC2

<p align=center>

</p>

## UC2 version history
When you search through the repository, you find that not all the images show the same cubes and baseplates. This is due to the evolution of the basic building blocks. In order to help you not to get lost, in the [Modular Developer Kit](../MDK#uc2-version-history) is a short explanation of how the cubes evolved.

#### v3 = 3D-printed AND Injection Moulded (*November 2020*)
This is the current version. The cube comes in two versions that are fully compatible with each other. You can either print all the baseplates and cubes and assemble and connect them using screws and magnets, or you can use the IM cubes and baseplate puzzles that connect via the lego-like pins.

The IM cube is shown on the left, the 3DP (3D-printed) cube is on the right. Find the details about the base cube in [ASSEMBLY_CUBE_Base](../CAD/ASSEMBLY_CUBE_Base).
<p align=center>


</p>

##  List of available Modules (CUBEs):
A list of available Cubes that are the building blocks of all our setups can be found in [CAD](../CAD).

### Complete overview of setups, modules, parts to buy and parts to print
Find a complete shopping'n'printing list including estimated prices for all modules and setups in this [GoogleDrive Spreadsheet](https://docs.google.com/spreadsheets/d/1U1MndGKRCs0LKE5W8VGreCv9DJbQVQv7O6kgLlB6ZmE/edit?usp=sharing)!

##  Participate
If you have a cool idea, please don't hesitate to contact us, we are happy to incorporate it in our design to make it even better.  
More setups are coming soon!
Inspire us with your ideas - we try to make it work! :-)

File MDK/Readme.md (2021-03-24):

# Modular Devoloper Kit - MDK

V3 – 30.11.2020 Benedict Diederich, Barbora Marsikova

If you want to adapt your ideas to the ***UC2*** framework this document provides you with all the necessary information. We provide a detailed description of the definitions, versions, intentions and files. Once you have introduced your idea into the system, please share it so that others can benefit from it!

The CAD templates can be found in the [CAD](./CAD)-folder.

All the original design files as well as all the STL files can be found is [CAD/RAW](../CAD/RAW).

### Definitions

The UC2 framework requires the introduction of several new concepts. These terms are defined in the table below and illustrated in a series of figures.

The Names can be found in the chart below (Fig 1). The chart also represents the logical structure of building a setup using UC2 elements.

The scheme describes the structure in which the toolbox is designed, therefore its explaining the naming convention of the design files (Inventor, openSCAD). There are a few differences between that and the repository CAD folder - those are noted in the table below.

<p align=center>

<br> <em>Fig. 1: Modular Developer Kit chart</em>
</p>

Name | Description
:---:|:---:
**CUBE (Baseplate)** | The **BASE puzzle pieces**, the basic units, are joined into the **BASEPLATE** (“skeleton” of the setups). The Baseplate can have any shape any size, depending on how many puzzles you use and how you put them together. It allows you to build setups in three dimensions when you 'sandwich' the layers of cubes and baseplates. This is the frame and backplane of the UC2 project, determining the size and layout of the optical system. 3D-printed UC2 modules attach to the square baseplate positions using ball-magnets and ferro-magnetic screws. The injection moulded cubes attach via their lego-like pins. Find the details of the baseplates on their [CAD page](../CAD/ASSEMBLY_Baseplate). *(Git: ASSEMBLY_Baseplate)*
**CUBE (IM)** | The injection moulded (IM) is a half of the cube. The **ASSEMBLY CUBE (empty)** cube is composed of these two identical halves and can be easily assembled by their press-fit mechanism. The assembled IM cube has two sides with eight lego-like pins each to attach to the baseplate. *(Git: ASSEMBLY_CUBE_BASE)*
**CUBE (Body)** | Alternatively, the whole cube can also be 3D-printed. Then the **ASSEMBLY CUBE (empty)** consist of the body- and the lid-part which get screwed together. Screws can be inserted on all sides in order to build setups in three dimensions.
**CUBE (Lid)** | The lid closes the 3D-printed cube when attached by screw to the body. It can carry electronics like microcontrollers (e.g. Arduino, ESP32). By adding wires to the screws closing the lid electronic components can be supplied with electrical power.
**ASSEMBLY CUBE (empty)** | The raw cube - the basic building block comes in two versions: 3D-printed and injection moulded. Both of them have the same dimensions and symmetry, so the insert fit them all. The similarities and differences of the two systems are explained under this table in the *UC2 version history section*. Note that the MDK only details the specification of the Cube and Base to the extent that it is necessary for module developers to develop modules. Find the details of the Cube on its [CAD page](../CAD/ASSEMBLY_CUBE_Base). *(Git: ASSEMBLY_CUBE_BASE)*
**CUBE INSERTS** | Cube Inserts are physical components that implement various functions into the system by adapting **EXTERNAL PARTS** to the **ASSEMBLY CUBE INSERT**. They fit the inner dimensions of the cube. There are two types of inserts: perpendicular (to the optical axis) and diagonal. They serve as holders for various components like  lenses, mirrors, cameras, filters, and other components demanded by the application. Existing inserts can be adjusted to fit specific parts (i.e. lens diameters).
**EXTERNAL PARTS** | Everything which is not part of the UC2-system or can not be 3D printed is termed as an EXTERNAL PART. This can be commercially available parts like objectives, lenses, LEDs, etc., but also 3D-printed parts from other projects (e.g. openflexure stage).
**ASSEMBLY CUBE (insert)** | This is the combination of the ASSEMBLY CUBE (empty) and a CUBE INSERTS. Since the ASSEMBLY CUBEs are the building blocks of a UC2 setup, adding features is accomplished by hardware plugins also called CUBE INSERTS.
**EXTERNAL MODULES** | Using EXTERNAL MODULES one adapt EXTERNAL PARTS that typically do not fit inside a cube but give function to it. This can be for example cellphones, stages projectors, etc. By providing customized hardware-adapter they interface with the ASSEMBLY CUBE.
**COMPLETE MODULES**  | Entire Functional modules that can be swapped to the system. They have the correct screws and dimensions to adapt to baseplate. They are fully independent, but follow the optical path (e.g. SIM-module, ISM-module, projector, etc.).
**APPLICATION** | APPLICATIONs are complete optical setups or microscopes. They are composed of several baseplate puzzles and modules with different functions. The GitHub-repository provides a list of basic optical systems which are also compiled into a ready-to-use list called "TheBOX".

### UC2 version history
When you search through the repository, you find that not all the images show the same cubes and baseplates. This is due to the evolution of the basic building blocks. In order to help you not to get lost, here is a short explanation of how the cubes evolved.
#### v3 = 3D-printed AND Injection Moulded
*November 2020*  
**This is the current version.** The cube comes in two versions that are fully compatible with each other. You can either print all the baseplates and cubes and assemble and connect them using screws and magnets, or you can use the IM cubes and baseplate puzzles that connect via the lego-like pins.

The IM cube is shown in the first picture. The two identical halves fit perfectly together and each of the two pinned sides of the cube fits to the baseplate.
<p align=center>

</p>

The 3D-printed cube is in the next picture. The body and the lid are held together by the M3 screws that attach to the magnets of the baseplate. Additionally, M5 screws are added to the position of the pins for better alignment precision.
<p align=center>

</p>

The 3D-printed baseplate puzzles are fully compatible with both types of cubes and with the IM puzzles. It is important to pay attention to calibration of your printer according to the guide in the [baseplate CAD page](../CAD/ASSEMBLY_Baseplate).

#### v2 = point symmetric
*July 2019*  
The v2 version looks pretty much like v3 without pins. The cube is point symmetric, therefore the insert can be used in various orientations. The baseplates have to be assembled in Inventor and printed in the desired size - mostly 4×1, 4×2, 4×4. The cube is also made of the Body and the Lid and can vary in size (e.g. 1×1, 2×1, etc.).  
They seem to be the same as the IM cubes - but not completely. The dimensions are slightly different. It isn't anything you couldn't fix with a file and sticky tape but it's advisable to use the matching cubes and inserts.
<p align=center>

</p>

You can still find a lot of pictures with v2 cubes in the GitHub - many of the applications we tested are simply shown in the version, which we first build them with.   
Knowing that it’s mechanically overdefined, the 4-point interface with screws and magnets gives the degree of freedom to level out mechanical imprecisions e.g. due to 3D printing etc. by adjusting the positions of the screws.

:grey_exclamation: If you are still working with the v2 version of the cube, you find the documentation in the [UC2_v2 branch](https://github.com/bionanoimaging/UC2-GIT/tree/UC2_v2).

#### v0 = the early cube
*2017*  
Why is there no v1? Because all the slow and steady development from the very beginning until the real modular microscopes is covered in this one. The v0 cube had a rail system similar to the cage system used by e.g. Thorlabs or Newport. The baseplate wasn't very different from v2.
<p align=center>

</p>
The old cube is not compatible with the current design and currently isn't shown anywhere in the repository.

#### Other versions
Have we tried other designs? Sure, we have. The cubes are nice to play with and nice for planning a setup but the design is mechanically over-determined. We tried to put the cube on [3-point connection](./CAD/ALTERNATIVE_DESIGN/UC2_with_3-holes-cubes) and use the [hexagonal building blocks](./CAD/ALTERNATIVE_DESIGN/UC2_with_Hexagonal_Block). Have a look at the attempts and issues to see why we stick with the cubes as they are.

<p align=center>


</p>

### Concept of the cube

The cube is the cornerstone of UC2 framework. Its purpose is to create a bridge between the toolbox and any external component. The cube itself is universal and thanks to the modular design of the inserts, it can be adapted for any application.

*   Interface to bridge UC2 and any external component
*   Dimensions of the "50 mm" Cube unit  
    *  The baseplate puzzle piece has the size of 50×50 mm<sup>2</sup>
    *   Distance from face to face is ~49,8 mm – to incorporate imprecision of the 3D-printer cube and to avoid adding up error in larger setups
    *   Distance from hole to hole (screws in the cube and magnets in the baseplate) 40 mm
*   (3DP) Screws in the cube fit on Ball magnets of the Baseplate
*   (IM) The pins of the cube fit into the holes of the baseplate
    *   The precise position of the pins is depicted in the schemes later on this page
*   Beam path is perpendicular and through center of the cube's faces
*   Centrosymmetric
*   Compatible with Thorlabs 1" Cage System
*   Function can be put into the cube by a special insert
*   Electronics
    *   The ESP32 can be controlled through WiFi and MQTT protocol

**IMPORTANT: Not all screws are magnetic!**  
It is very important to buy the right screws - the M3 screws need to attach to the magnets and therefore it is crucial that they are magnetic. STAINLESS STEEL IS GENERALLY NOT A MAGNETIC MATERIAL. THE SCREWS HAVE TO BE MADE OF GALVANIZED STEEL. If you want to know more about why not all steel is magnetic you can read about it [here](https://monnigindustry.com/2020/12/23/is-galvanized-steel-magnetic-why-or-why-not/). Unfortunately, the DIN 912 / ISO 4762 screws that we propose can be made of both and you can frequently find both at the same vendor.    
The take-home message is: **The M3 screws have be made of galvanized steel and never stainless steel!**  
Check out the [RESOURCES](../TUTORIALS/RESOURCES/Resources_Mechanics.md) for sources of the right screws.

<p align="center">

<br><em>Fig. 2: Basic empty cube - Injection Moulded (IM)</em>
</p>

<p align="center">

<br><em>Fig. 3: Basic empty cube 1×1 - 3D-printed (3DP)</em>
</p>

<p align="center">

<br><em>Fig. 4: Basic empty cube 2×1 (3DP)</em>
</p>

### Concept of the Baseplate

The Baseplate is the “skeleton” of the UC2 framework and holds the different modules in place and in given mutual position. The baseplate is made of its single units - baseplate puzzles. The Baseplate can have any shape any size, depending on how many puzzles you use and how you put them together. It allows you to build setups in three dimensions when you 'sandwich' the layers of cubes and baseplates.  
The baseplate puzzles are the same whether you print them with a 3D printer or whether you use the IM ones. They can also be freely combined together.  
For attaching the 3DP cubes, you just add magnets in the designated holes of the puzzle piece. The ball magnets are pressed fit into the 3DP or IM baseplate.

<p align="center">

<br><em>Fig. 5: Baseplate and setup building - top view</em>
</p>

<p align="center">

<br><em>Fig. 6: Baseplate and setup building - perspective view</em>
</p>

So far it’s designed the way, that ball-magnets are pressed fit into the 3D printed baseplate which interact with the 3D printed cubes.   

*   Baseplates puzzles can be arbitrarily combined into large or small baseplates
*   Holes for pins to create a stable lego-like connection between the cube and the baseplate
* Holes for 5mm ball magnets (press fit) to attach to the 3DP cube
*   Dimensions:
    *   Base-plate unit: 50×50 mm<sup>2</sup>
    *   Distance: Magnet-Magnet: 40 mm
*   Additional holes for M6 screws to adapt to e.g. metallic (bread) boards (e.g. Thorlabs grid). Distance is 50-50mm
*   Module finds its place on a grid
*   The system can be built in the 3<sup>rd</sup> dimension by sandwiching layers of cubes and baseplates

### Building a UC2_v3 setup
#### Watch the videos in the [UC2_v3 playlist](https://www.youtube.com/playlist?list=PLB7sYInE0vsM_uuHkdbQfF4FY6i0mnbqv) to see how it works!

* The 3DP baseplate puzzles (pink) and IM baseplate puzzles (black) can be combined and one large baseplate can be build using both types.
<p align="center">


</p>

* The 3DP baseplate puzzles (black) and IM Cube (right) can be used in parallel in the same setup. The IM Cube connects to the baseplate via eight lego-like pins on top and bottom side. The 3DP Cube connect with its screws in the corners to the magnets of the baseplate. Additionally, it has three M5 screws that work like the pins of the IM Cube, for better precision of alignment.
<p align="center">

</p>

* The baseplate puzzle can be build into a baseplate of arbitrary shape and size in 2D. Layers of baseplates and cubes can be sandwiched into a three-dimensional setup.
<p align="center">

</p>

#### Watch how much time the IM cubes can save!
UC2 YouSeeToo - IM and 3DP cube comparison (https://www.youtube.com/watch?v=M_oqieogAOo&feature=youtu.be&ab_channel=openUC2)

### Good Practice to transfer an optical system to UC2

*   Fourier optics is happy if the focal lengths of adjacent lenses follow each other (minimizing vignetting, telecentric systems, etc.)
*   Lenses should be chosen as integer 50 mm of their focal lengthes (ideal lens, real lens => subtract thickness of the lens itself=> focal point -focal point 100mm)
*   Think in modules and blocks
*   Divide functions in submodules
*   Concatenate submodules to functions
*   A subunit can be extended in integer of 1x1 cubes in XYZ
*   Example: A simple telescope can be accomplished by concatenating two lenses (50mm, 100mm) with a distance of 150mm wrt. their back-focal length (BFL) – see figure 5
*   If a function cannot be realized by concatenating cubes/submodules, a dedicated module can be developed which itself interfaces to an existing bigger setup (e.g. a module which holds a video-projector

<p align="center">

<br><em>Figure 5: Scheme of two of the possible modular setups: Top: Keplerian telescope; bottom: Smartphone microscope.</em>
</p>

#### Template for UC2-designs

We incorporated a PPT-based layout helper for the creation of arbitrary complex system using UC2. Go to the [PPT](./PPT) Folder and open the file [UC2_Setupcreation.pptx](./PPT/UC2_Setupcreation.pptx) which has  slides for all available components:

<p align="center">

<br><em>Figure 5a: Available UC2 components.</em>
</p>

 and the baseplate to place the components on it in order create the setup:

<p align="center">

<br><em>Figure 5b: Playground for the UC2 setup creation.</em>
</p>

You can also use the publicly available tool [draw.io](https://app.diagrams.net/). Simply import our libraries from the [DRAW.IO](./DRAW.IO) Folder. You find there one for the schemes - [UC2_schemes](./DRAW.IO/UC2_schemes.xml) (same as in the .ppt) and one for the SIMPLE sketches - [UC2_simple](./DRAW.IO/UC2_simple.xml).

### Cube Inserts

The cube inserts can be fully customized to adapt any optical element to the cubes. So far a perpendicular and diagonal version exists. The design files for Autodesk Inventor and OpenSCAD are available. Once you have a customized version, please share it so that the open-aspect of the system reaches its full potential :)

Since the cube is point symmetric around the origin, the inserts can be rotated in all directions and bridges external components to the modules by acting as an open-standard.

The CAD templates for Autodesk Inventor 2019 (```.ipt```) and ```STL/STEP```-standard can be found in the [CAD](./CAD)-folder.

##### Cube Insert (Perpendicular)

*   This can be slided into the cube
*   Allows variation in the position along the optical axis, three different orientations of the insert inside the cube are possible
*   Important are the following distances:
    *   from one inner edge of the cube to its opposite counterpart (54,0 mm)
    *   the thickness of the inner edge of the cube is 6,20 mm
    *   plate thickness: 5,0 mm (optimal for most modules - provides enough freedom as well as stability)
*   The insert is gripped by a form-fit mechanism – eventually adjust the size when printing the insert so that it fits smoothly
*   Example for an insert which adapts a Thorlabs Cage Components (CP02)
*   An Example is given [here](./CAD)

##### Cube Insert (Diagonal)

*   This can be slided into the cube
*   Allows variation in the position with an angle of 45° w.r.t. the optical axis
*   Important are the following distances:
    *   from one inner edge of the cube to its opposite counterpart (54,0 mm)
    *   the thickness of the inner edge of the cube is 6,20 mm
*   The insert is gripped by a form-fit mechanism – eventually adjust the size when printing the insert so that it fits smoothly
*   Example for an insert which adapts a 30×30 mirror
*   An Example is given [here](./CAD)

### CAD Drawings

##### Baseplate

<p align="center">

</p>

##### Cube Body

<p align="center">

</p>

##### Cube Lid

<p align="center">

</p>

##### Cube Insert (Perpendicular to the optical axis; Thorlabs cage system compatible) - Sample holder

<p align="center">

</p>

**Video Tutorial on How to design a Cube Insert (Perpendicular to the optical axis)**  
**The tutorial shows a v2 insert - the principle is the same but the dimensions differ!**

UC2 YouSeeToo - How to design an insert (https://www.youtube.com/watch?v=q2DNw-Q1KEo&t=2s)

##### Cube Insert (Diagonal) - 45° Mirror holder

<p align="center">

</p>

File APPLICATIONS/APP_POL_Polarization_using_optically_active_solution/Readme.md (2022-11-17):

# Polarization Experiment using Optically Active Solution

<p align="center">

</p>

The optical activity was discovered by Arago in the quartz in 1811. In 1847, molecular chirality was observed by scientist Louis Pasteur. He found that natural tartaric acid is optically active, and its external crystals have isomerism and chiral morphology *[1]*.

Two molecules with the same chemical formula, the mirror image of the other, describe molecular chirality. These come in two varieties: dextrorotatory (rotate plane-polarized light clockwise) and levorotatory (counterclockwise).

Sucrose is a disaccharide made of glucose and fructose and dextrorotatory, which rotates the plane-polarized light to the right. A well-known example of sucrose is table sugar produced naturally in plants. Fructose is a simple ketonic sugar and levorotatory which rotates the plane-polarized light to the left. Glucose is a simple sugar that belongs to the carbohydrate family and is dextrorotatory. The molecules of fructose and glucose are mirror images of each other. Corn syrup is one of the most commonly used sugar solutions *[2]*.

Two simple sugar-water solutions were prepared and used in the experiment. The first solution was produced with one cup of table sugar and one cup of water. Table sugar is sucrose and dextrorotatory, turning clockwise to the right plane-polarized light. Grape sugar is dextrorotatory and glucose, and the second solution mixes grape sugar (Traubenzucker) and water components in the same amount. It rotates the incoming light polarization state to the right, clockwise direction. However, two solutions have different polarization states at the same time because of their molecular structure and demonstrate different colors inside the crossed polarizers.

<p align="center">

</p>

In the image, Table sugar-water solution is shown in left-side, Grape sugar-water solution is in the right glass.

## Parts

### Modules for this setup

|  Name | Properties  |  Price | Link  | # |
|---|---|---|---|---|
|  4×1 Baseplate | Skeleton of the System | 5.47 €  | [Base-plate](../../CAD/ASSEMBLY_Baseplate)  | 1 |
|  MODULE:  *Polarizer Cube* | It holds the linearly polarizing filter  |  8.62 €  | [Linear Polarizer](../../CAD/ASSEMBLY_POL_Linear_Polarizer)  | 2 |
|  MODULE:  *Active Solution Chamber* | It contains sugar-water solutions.  |  7.32 €  | [Active Solution Chambers](../../CAD/ASSEMBLY_POL_Active_Solution_Chamber)  | 1 |
|  EXTRA MODULE: Flashlight Lamp Cube | Light Source  | 7.2 €  | [Flashlight](../../CAD/ASSEMBLY_CUBE_Flashlight)  | 1 |

### Parts to print

* 1 × [Base-plate 4×1](./STL/Assembly_Cube_Baseplate_4x1_v2.stl)
* 2 × [Cube base 1×1](./STL/10_Cube_1x1_v2.stl)
* 2 x [Cube lid 1×1](./STL/10_Lid_1x1_v2.stl)
* 2 × [Polarizer Guide](./STL/20_POL_Cube_Insert_Linear_Polarizer_Guide.stl)
* 2 × [Polarizer Wheel](./STL/20_POL_Cube_Insert_Linear_Polarizer_Wheel.stl)
* 2 × [Polarizer Lid](./STL/20_POL_Cube_Insert_Linear_Polarizer_Lid.stl)  
* 1 × [Cube Lid 2x1](./STL/10_Lid_el_2x1_v2.stl)
* 1 x [Active Solution Chamber - Alternative 1 with Two Sections](./STL/10_POL_Active_Solution_Chamber_90long_40High_Double_TOP.stl)
* 1 x [Active Solution Chamber - Alternative 2 with One Sections](./STL/10_POL_Active_Solution_Chamber_90long_40High_TOP.stl)    
__*Extra Holder Parts but NOT USED in our experiment:*__
* 1 × [Flashlight Holder](./STL/20_Cube_Insert_Holder-okular+flashlight_v2.stl)

<p align="center">

</p>  

##  Additional components
* Check out the [RESOURCES](../../TUTORIALS/RESOURCES) for more information!
* 1 × Linear Polarizing Sheet [🢂](https://amazon.de/-/en/Polarizing-A4-Sheet-Polarizer-Educational-Polarized/dp/B06XWXRB75/ref=pd_sbs_421_3/262-2115536-7173904?_encoding=UTF8&pd_rd_i=B06XWXRB75&pd_rd_r=b88e7340-b061-4e0b-8daa-8ec533fd7c71&pd_rd_w=qlkAY&pd_rd_wg=At9EZ&pf_rd_p=a03ac387-6e4d-4f6b-96b6-1853da0bb37b&pf_rd_r=49HX2Z4Q5KRZSQ2FWRQR&psc=1&refRID=49HX2Z4Q5KRZSQ2FWRQR)
* 24 × 5 mm Ball magnets [🢂](https://www.magnetladen.de/kugelmagnet-5-mm-n42-nickel/)
* 20 x Screws DIN912 ISO 4762 - M3×12 mm [🢂](https://eshop.wuerth.de/Zylinderschraube-mit-Innensechskant-SHR-ZYL-ISO4762-88-IS25-A2K-M3X12/00843%20%2012.sku/de/DE/EUR/)
* 6 x Screws DIN912 ISO 4762 M2×16 mm [🢂](https://www.amazon.de/Edelstahl-Sechskopf-Knopf-Schrauben-Unterlegscheiben-Sortiment-Aufbewahrung/dp/B073SS7D8J/ref=sr_1_fkmr0_1?__mk_de_DE=%C3%85M%C3%85%C5%BD%C3%95%C3%91&keywords=zylinderkopfschrauben+set+galvanisiert&qid=1565007371&s=diy&sr=1-1-fkmr0)
* 2 x metal plates
* Microscope Rectangular Coverslips [🢂](https://www.ebay.de/itm/223260964391?hash=item33fb63f627:g:pukAAOSwsGpb%7E14N)
* _NOT USED_ 1 × flashlight [🢂](https://www.pollin.de/p/led-taschenlampe-alu-5-w-cree-led-3xmicro-schwarz-b-ware-535448)

##  Assembly

* [Baseplate](../../CAD/ASSEMBLY_Baseplate)
* [Linear Polarizer Cube](../../CAD/ASSEMBLY_POL_Linear_Polarizer)  
* [Active Solution Chambers](../../CAD/ASSEMBLY_POL_Active_Solution_Chamber)  
__*EXTRA MODULE:*__
* [Flashlight cube](../../CAD/ASSEMBLY_CUBE_Flashlight)

<p align="center">

</p>  

##  Results

We printed and assembled two Linear Polarizer and Active Solution Chamber module parts. Then, we bought the necessary components and inserted them into cubes.  
You can see the datils of the Active Solution Chamber designs.

<p align="center">

</p>

<p align="center">

</p>

Two different chamber design is shown in the image below. Left-side chamber has a container only for 1 active solution. In the other one, two different mixtures can be observed in the same time.  

<p align="center">

</p>

You can find the basic version of Polarization Using Optically Active Solution experiment with an additional flashlight source below.  Depends on the experiment place conditions, you can add an extra light source.

<p align="center">

</p>

The chamber module was inserted between two linear polarizers, the Crossed Polarizers. We can observe the direct effect of the angle between two linear polarizers in the video below. The intensity of passing light through crossed polarizers changes when the direction angle of the polarization filter changes 360 degrees.

Experimental result of two optically active solutions is shown in the video:      
   *  Left Is Grape Sugar-water Solution (Glucose) Table,          
   * Right Is Sugar-water Solution (Sucrose

<p align="center">

</p>

## References

[1] Gal, J. (2017). Pasteur and the art of chirality. Nature Chemistry, 9(7), 604–605. https://doi.org/10.1038/nchem.2790    

[2] Logiurato, F. (2018). Teaching Light Polarization by Putting Art and Physics Together. The Physics Teachers, 1–5. https://arxiv.org/ftp/arxiv/papers/1803/1803.09645.pdf

## New Ideas
We are open to new ideas. Please contribute the project freely, this place is a free country which is built by codes and machines :robot:

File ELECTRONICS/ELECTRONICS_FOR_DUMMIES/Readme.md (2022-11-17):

# Electronics (for dummies)

Don't have much experience with electronics? It's actually really simple!

##  Components
* LED-Array, Neopixel, 8x8 [🢂](https://www.amazon.de/AZDelivery-Matrix-CJMCU-8-Arduino-Raspberry/dp/B078HYP681/ref=sr_1_2?__mk_de_DE=%C3%85M%C3%85%C5%BD%C3%95%C3%91&keywords=neopixel+matrix&qid=1565008576&s=gateway&sr=8-2)
* ESP32 [🢂](https://www.amazon.de/AZDelivery-NodeMCU-Development-Nachfolgermodell-ESP8266/dp/B074RGW2VQ/ref=sr_1_3?__mk_de_DE=%C3%85M%C3%85%C5%BD%C3%95%C3%91&keywords=esp32&qid=1565008313&s=gateway&sr=8-3)
* Stepper Motor and Driver Board [🢂](https://www.amazon.de/Elegoo-Stepper-Schrittmotor-28BYJ-48-Treiberplatine/dp/B01MEGIHLF/ref=sr_1_1_sspa?__mk_de_DE=%C3%85M%C3%85%C5%BD%C3%95%C3%91&keywords=stepper+arduino&qid=1565008205&s=gateway&sr=8-1-spons&psc=1)
* Female-Female Jumper Wire, 0.14 mm² [🢂](https://www.amazon.de/-/en/Dupont-jumper-Arduino-Raspberry-projects/dp/B09KGRM98K/ref=sr_1_5?crid=7W47OEJ8252N&keywords=br%C3%BCckendraht+weiblich+weiblich+0%2C14&qid=1668724084&s=industrial&sprefix=female-female+jumper+wire+0.14%2Cindustrial%2C488&sr=1-5)
* Power cables for ESP32 - USB-microUSB [🢂](https://www.amazon.de/dp/B0778FV6K4/ref=sr_1_2?dchild=1&fst=as%3Aoff&qid=1586361990&refinements=p_89%3AGritin&rnid=669059031&s=computers&sr=1-2)

##  Connecting the electronics

* When using [jumper wires](http://blog.sparkfuneducation.com/what-is-jumper-wire) you can avoid most of the soldering.

#### **LED array** - 3 wires

<p align="center">

</p>

Connect everything - mind the right pins!

* The wires connect to the little trident which goes into the LED array
* Their other ends connect to the ESP32 according to the scheme above

<p align="center">






</p>

#### **Z-stage** or **Sample-stage** - 6 wires + motor connection
* Sample stage is the very same as the Z-stage - you just mount it on different 3Dprinted parts.

<p align="center">

</p>

Connect everything - mind the right pins!

* Connect the motor to the driver board
* Two of the wires are for the (+) and (-)
* Four of the wires are for the IN1 - IN4 (inputs)
* Their other ends connect to the ESP32 according to the scheme above

<p align="center">






</p>

* Flash them with the right software from our [Software-GIT](https://github.com/bionanoimaging/UC2-Software-GIT).
* Power the ESP32 simply with microUSB cables.
* And it works just like that ;-)

## Electronics for the SIMPLE smartphone microscope
No control via WiFi - just buttons. The Simple Smartphone Microscope is found [here](../../APPLICATIONS/APP_SIMPLE-Smartphone_Microscope/electronic)

* When using jumper wires you can avoid soldering.
* LED array - 3 wires + 2 wires for the button

<p align="center">

</p>

* Z-stage - 6 wires + motor connection + 2×2 wires for two buttons

<p align="center">

</p>

* The buttons are simply an add-on to the Electronics - connect to wires to each button and to the correct pins of the ESP32
<p align="center">




</p>

* Power the ESP32 simply with microUSB cables.
* And it works just like that ;-)

Further advice:  
[But I don't have such wires...](https://www.youtube.com/watch?v=VB1CrqY_jMg)  
[But how to connect two wires to the same pin?](https://www.youtube.com/watch?v=8W-zdo1AVns)

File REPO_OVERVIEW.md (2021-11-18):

#  Overview of the openUC2 projects and repositories

## The main repositories:

* [UC2-GIT](https://github.com/openUC2/UC2-GIT) - This is the main repository. This one right here.

* [UC2-Software-GIT](https://github.com/openUC2/UC2-Software-GIT) - This repository hosts all necessary software for the UC2 project.

* [uc2-configurator](https://github.com/openUC2/uc2-configurator) - (in development) webapp that allows for easily downloading relevant stl files for the uc2 system

## UC2-based hardware projects and more complex systems:

* [UC2_project_template](https://github.com/openUC2/UC2_project_template) - If you're starting a separate UC2-based project, please document it in a repository that follows this structure.

* [UC2_openSIM](https://github.com/openUC2/UC2_openSIM) - This is the repository for the openSIM project which integrates structured illumination microscopy into the UC2-system.

* [UC2_openISM](https://github.com/openUC2/UC2_openISM) - This is the repository for the openISM project which integrates a laser-scanning module for image-scanning microscopy (ISM) to the UC2-system.

* [UC2-MicronStage](https://github.com/openUC2/UC2-MicronStage) - UC2 micrometer stage

* [UC2-Hi2](https://github.com/openUC2/UC2-Hi2) - This device is intended to help you use a very simple GRBL-based Arduino Shield controlled by a Raspberry Pi/Nvidia Jetson to automatically image a multiwell plate to with a UC2-based microscope.

* [UC2_Fluorescence_microscope](https://github.com/openUC2/UC2_Fluorescence_microscope) - This is the repository for the laser-based fluorescence microscope with infinity optics. It is capable to acquire Time-Lapse videos from living cells inside an incubator.

* [UC2-Ptycho](https://github.com/openUC2/UC2-Ptycho) - A first attempt to create a UC2 system that is creating Ptychography Data

* [UC2_openKOEHLER](https://github.com/openUC2/UC2_openKOEHLER) - This is the repository for the openKOEHLER project which integrates an adaptive diaphragm (e.g. variable effective light-source plane) in Koehler configuration into the UC2-system.

## UC2 goes ARRR! (Augmented Reality project - related repositories)

* [UC2-AR-RECOGNITION](https://github.com/openUC2/UC2-AR-RECOGNITION) - Recognition models and tests used for the AR-recognition framework. This repository will be fused into the final AR-repo once enough development is done.

* [UC2-AR-APP](https://github.com/openUC2/UC2-AR-APP) - All AR app related stuff will come in here.

## Others

* [UC2-ImJoy-Plugins](https://github.com/openUC2/UC2-ImJoy-Plugins) - This is a collection of ImJoy Plugins which could be used for the UC2 Framework.

* [UC2_OFM-extensions](https://github.com/openUC2/UC2_OFM-extensions) -

* [UC2-Hackathon](https://github.com/openUC2/UC2-Hackathon) - 2nd Photonics Days Makethon: Digital concept for university internships in physics and optics

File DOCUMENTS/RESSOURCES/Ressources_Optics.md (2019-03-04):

## Resources: Optics

We cannot guarrantee the availability of the components. If you know other components, please let us know by filing an issue. Thank you :-) 

### Objective Lenses
|  Name | Properties  |  Price | Link  | Tested |
|---|---|---|---|---|
|  Amscope | 10x, NA=.25, TL=160mm  | 35€  | [Amazon](https://www.amazon.de/amscope-Plan-Achromatisches-Objektiv-ger%C3%A4ndelten/dp/B01G4CCB8G/ref=sr_1_6?ie=UTF8&qid=1542893150&sr=8-6&keywords=amscope+10+x+objektiv)  | Yes |
|  Optika | 20x, NA=0.40, infinity, N-plan, POL  | 95€  | [Optics-Pro](https://www.optics-pro.com/for-microscopes/optika-objective-20x-0-40-infinity-n-plan-pol-b-383pol-m-146p/p,56893)  | Yes |
|  Müller | Plan 100x, NA= 1.25 Öl, TL=160, Correction=0.17 | 65€  | [Benad24](https://www.benad24.de/business-industrie/produktions-industriebedarf/medizin-labor-laborgeraete/mueller-objektiv-plan-100-1-25-oel-160-0-17-fuer-biologisches-mikroskop/a-1234576610/)  | Yes |
|  Unknown | Finite corrected, 4X 10X 20X 40X 60X 100X Achromatic Objective  | 10-135€  | [Aliexpress](https://www.aliexpress.com/item/1-set-4X-10X-20X-40X-60X-100X-Biological-Microscope-Objectives-Achromatic-lens-Free-shipping/32651361216.html?spm=2114.search0104.3.2.75af66d5taUTYa&ws_ab_test=searchweb0_0,searchweb201602_2_10065_10068_10130_5734615_10890_5730315_10547_10546_319_10548_317_5734813_10545_10696_5734713_10924_453_10084_454_10083_10618_10920_5729215_10921_10922_10307_537_536_10059_10884_10887_10928_100031_321_322_10103_5734515-5734615,searchweb201603_51,ppcSwitch_0&algo_expid=fc1adc20-26ab-43ce-b980-de2409614405-0&algo_pvid=fc1adc20-26ab-43ce-b980-de2409614405)  | Yes |
|  Unknown | Infinity corrected, 4X 10X 20X 40X 60X 100X Achromatic Objective  | 10-135€  | [Aliexpress](https://www.aliexpress.com/item/Professional-Full-Set-4X-10X-40X-100X-Achromatic-Plan-Infinity-Objective-Lens-195mm-Biological-Microscope-Objective/32837671031.html?spm=2114.search0104.3.2.570c678ewq3tmI&ws_ab_test=searchweb0_0,searchweb201602_2_10065_10068_10130_5734615_10890_5730315_10547_10546_319_10548_317_5734813_10545_10696_5734713_10924_453_10084_454_10083_10618_10920_5729215_10921_10922_10307_537_536_10059_10884_10887_10928_100031_321_322_10103_5734515,searchweb201603_51,ppcSwitch_0&algo_expid=fa024651-2d77-4fad-867c-8cd8bcf06f4c-0&algo_pvid=fa024651-2d77-4fad-867c-8cd8bcf06f4cde2409614405)  | No |
|  South Optics | Infinity corrected, 4X 10X 20X 40X 60X 100X Achromatic Objective  | 10-135€  | [South Optics](http://www.southoptics.com/website/wbsAction_loadPages.action?ssid=59&pssid=29%3E)  | No |
|  Motic | Motic Objektiv CCIS plan achromat. EC-H PL 4x/0.1 (AA=15.9mm)  | 101€  | [Astro Media](https://www.astroshop.de/fuer-mikroskope/motic-objektiv-ccis-plan-achromat-ec-h-pl-4x-0-1-aa-15-9mm-/p,45939)  | No |
|  Motic |Motic Achromat. Klapp-Kondensor N.A. 0,90/0.13 mit irisblende  | 150€  | [Astro Media](https://www.astroshop.de/kondensoren/motic-achromat-klapp-kondensor-n-a-0-90-0-13-mit-irisblende/p,51901)  | No |

Most Objectives come with an RMS thread. 

We highly recommond you to check the marketin with known retaillers (e.g. eBay, Amazon, Aliexpress, Alibaba). We made good experience with the low-cost optics!

### Lenses
|  Name | Properties  |  Price | Link  |
|---|---|---|---|
| Convex  |  Various |  1-10 € | [Optik Baukasten](http://optik-baukasten.de/)  |
| Concave |   Various  |  1-10 € |  [Optik Baukasten](http://optik-baukasten.de/) |
| Generic  |  Various |  10-30 € | [Thorlabs](https://www.thorlabs.com/newgrouppage9.cfm?objectgroup_id=4847)  |
| Generic  |  Achromatic (Examplary) |  10-30 € | [Aliexpress](https://www.aliexpress.com/item/Diameter-25-4MM-Focal-Length-75-MM-Visible-Achromatic-Double-Lenses/32639546486.html?spm=2114.search0104.3.14.18c63065jIMhZ2&ws_ab_test=searchweb0_0,searchweb201602_3_10065_10068_10130_10890_10547_319_10546_317_10548_10545_10696_453_10084_454_10083_433_10618_431_10307_537_536_10902_10059_10884_10887_100031_321_322_10103,searchweb201603_6,ppcSwitch_0&algo_expid=3a529ed2-2a9f-4b0c-a5a1-94621e27e468-2&algo_pvid=3a529ed2-2a9f-4b0c-a5a1-94621e27e468&transAbTest=ae803_3)|
| Generic  |  Various (They used to have a large variety) |  10-30 € | [Astromedia](https://www.astroshop.de/?q=achromat)
| Generic  |  Achromatic (Examplary) |  10-30 € | [Ebay](https://www.ebay.de/itm/2pcs-Optiche-Glas-Optik-vergroserungsglas-Doublet-Achromatische-Bikonvex-Linse/172633857864?hash=item2831c79f48:m:mb2CJPQUTT-XAcOtMdZpRpw:rk:4:pf:0)
| Generic  |  Biconvex (Examplary) |  8 € | [Amazon](https://www.amazon.de/UEETEK-Brennweite-Durchmesser-Optische-Glaslinse/dp/B077N8YTGG/ref=sr_1_1?ie=UTF8&qid=1548691473&sr=8-1&keywords=Konkave+Linsen)
| Generic  |  Concave (Examplary) |  5 € | [Amazon](https://www.amazon.de/Blesiya-Physisches-Laborbedarf-Wissenschaft-Experiment/dp/B07GJW6J83/ref=sr_1_6?ie=UTF8&qid=1548691473&sr=8-6&keywords=Konkave+Linsen)
| Generic  |  Achromatic (Examplary) |  20 € | [Amazon](https://www.amazon.de/Durchmesser-Brennweite-95-K9-plano-concave-Objektiv-konkaver/dp/B013SN312E/ref=sr_1_17_sspa?ie=UTF8&qid=1548691550&sr=8-17-spons&keywords=Konkave+Linsen&psc=1)
| Generic  |  Various (Examplary) |  20 € | [Amazon - Ajax Scientific Shop](https://www.amazon.de/s/ref=bl_dp_s_web_0?ie=UTF8&search-alias=aps&field-keywords=Ajax+Scientific)

### Mirrors and Others
|  Name | Properties  |  Price | Link  |
|---|---|---|---|
| Prisms/Beamsplitters  |  Various |  10-30 € | [Optik Baukasten](http://optik-baukasten.de/)  |
| Mirrors | 1 inch Mirrors to replace Thorlabs parts |  5-10 € | [Aliexpress](https://www.aliexpress.com/item/3Pcs-Free-Shipping-Mo-Reflective-Mirror-Dia-25mm-Molybdenum-Reflector-Lens-For-CO2-Laser-Cutting-Engraving/32759696170.html?spm=2114.search0104.3.2.167975efSJYug2&ws_ab_test=searchweb0_0,searchweb201602_2_10065_10068_10130_5734615_10890_5730315_10547_10546_319_10548_317_5734813_10545_10696_5734713_10924_453_10084_454_10083_10618_10920_5729215_10921_10922_10307_537_536_10059_10884_10887_10928_100031_321_322_10103_5734515,searchweb201603_51,ppcSwitch_0&algo_expid=5f5516e3-337b-4ea3-9625-bb82c9a6c350-0&algo_pvid=5f5516e3-337b-4ea3-9625-bb82c9a6c350)  |
| Grating (Tranmission) |  1000 l/mm |  5 € | [Astro Media](https://experimentis-shop.de/beugungsgitter-fuer-optische-versuche-detail-441.html)  |
| Prism |  Generic |  10 € | [Amazon](https://www.amazon.de/dp/B0716T8KS4/ref=sspa_dk_detail_2?psc=1&pd_rd_i=B0716T8KS4&pd_rd_w=LKu5R&pf_rd_p=00903874-3af0-47e0-8622-ee58087f71cf&pd_rd_wg=SNXHK&pf_rd_r=WXGT2NAAVMTR9QDASTY2&pd_rd_r=8b223bf8-2316-11e9-bb57-2164ec7a06dc)  |
| Dichroic Prism/BS |  Generic |  10 € | [Amazon](https://www.amazon.de/Askliy-Physik-Pr%C3%A4zision-optisch-Prisma/dp/B01LSATQI2/ref=pd_bxgy_328_img_2?_encoding=UTF8&pd_rd_i=B01LSATQI2&pd_rd_r=eadee6fe-2316-11e9-9f91-fdda01699348&pd_rd_w=4rz9k&pd_rd_wg=wDsca&pf_rd_p=c63cca93-7a15-40dd-b68a-47167d2b2080&pf_rd_r=RMDXQTSY6WHWMVE03SGS&psc=1&refRID=RMDXQTSY6WHWMVE03SGS)  |

### Filters 
|  Name | Properties  |  Price | Link  |
|---|---|---|---|
| Fluorescent Filters  |  Various |  10-30 € | [Comar Filters](https://www.comaroptics.com/components/filters/)  |
| Dichroics  |  Various |  10-30 € | [Comar Filters](https://www.comaroptics.com/components/filters/)  |
| Long-/Band-pass filters  |  Various |  10-30 € | [Comar Filters](https://www.comaroptics.com/components/filters/)  |
| Rosco Gel Filters |   Various |  10-30 € | [RoscoLux Filters](http://www.rosco.com/filters/roscolux.cfm)  |

A set of excellent resources for proper low-cost filter selection can be found here:

Gel-Filters (mostly from Roscolux):
[Kurt Thorn' Blog](http://nic.ucsf.edu/blog/2013/10/theatrical-gels-as-color-filters/)

Gel-Filters Case scenario [Wormlab](http://post.queensu.ca/~chinsang/lab-protocols/gfp-stereoscope.html)

[GFP (with # for ordering the parts):](https://makezine.com/2011/03/04/cheap-diy-gfp-green-fluorescent-protein-illuminator/)

[Comar Interference Filters:](https://github.com/OpenLabTools/Imaging_RPi_Fluorescence/blob/master/content.md)

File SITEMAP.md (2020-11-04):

#  Site map for easy navigation

## [Main page with the story of UC2](./Readme.md)

* [Making open-science great again!](https://github.com/bionanoimaging/UC2-GIT#making-open-science-great-again)
* [UC2 as an "open-standard"](https://github.com/bionanoimaging/UC2-GIT#uc2-as-an-open-standard)
* [License](./License.md)
* [Showcase](https://github.com/bionanoimaging/UC2-GIT#showcase)
* [Credits](https://github.com/bionanoimaging/UC2-GIT#credits)

There you also find our

* [Code of conduct](./CODE_OF_CONDUCT.md)
* [Contributor guidelines](./CONTRIBUTING.md)

 ## [Applications](./APPLICATIONS)

 [HERE](./APPLICATIONS) you find all the setups that have already been built.

 ## [CAD](./CAD)

 [HERE](./CAD) you find all the cubes and modules that are the building blocks of the [setups](./APPLICATIONS).  
 Each cube has its own:

 * function description
 * list of 3D printed parts (STL folders)
 * list of additional components that you need to buy
 * assembly tutorial

 ## [Electronics](./ELECTRONICS)

 [HERE](./ELECTRONICS) you will find guidelines for the electronic parts that are used in several cubes and other related stuff.  
 The discussed topics are:

 * [Z-stage and Sample-Stage](./ELECTRONICS/Z-Stage)
 * [LED matrix](./ELECTRONICS/LED-Matrix)
 * [Fluo-LED for Z-stage](./ELECTRONICS/FLUO-LED)
 * [XY-Stage](./ELECTRONICS/XY-Stage)
 * [Raspberry Pi](./ELECTRONICS/RASPBERRY-PI)
 * [Magnetic connectors (v0)](./ELECTRONICS/Magnetic-Connectors)

 There is also a simplified guide [Electronics for dummies](./ELECTRONICS/ELECTRONICS_FOR_DUMMIES).

 ## [MDK](./MDK)

 [HERE](./MDK) you find the Modular Developer Kit. If you want to adapt your ideas to the UC2 framework the Modular Developer Kit gives you the necessary steps in order to do so. We provide detailed description of the definitions, intentions and files. There you also find the templates and CAD drawings.

 ## [Software](./SOFTWARE)

All software can be found in the dedicated [UC2-Software-GIT](https://github.com/bionanoimaging/UC2-Software-GIT) repository.  
There is also a dedicated [UC2+ImJoy Image Processing](https://github.com/bionanoimaging/UC2-ImJoy-Plugins) repository.

 ## [The BOX](./TheBOX)

 [HERE](./TheBOX) you find our BOXes. The BOX is a comprehensive toolbox that contains a given set of cubes and can be used for a series of experiments.  
 Currently, we have three levels:

 * [SimpleBOX](./TheBOX/SimpleBOX) for schools and demonstration of basic optical principles
 * [FullBOX](./TheBOX/FullBOX) for adventurous biologists and microscopy enthusiasts
 * [CourseBOX](./TheBOX/CourseBOX) for Basic Microscopy and Optical Alignment courses

 ## [Tutorials](./TUTORIALS)

 [HERE](./TUTORIALS) you find a step-by-step guidelines that will lead you through the UC2 toolbox. From the level of total beginners you can follow the steps to become a contribute or spread the idea in your school or research institution.  
 The guidelines are divided into sections:

 * [First steps](./TUTORIALS#-first-steps) - getting familiar with hardware and software
 * [Tutorials](./TUTORIALS#-tutorials) - detailed guidelines for your first steps through UC2
 * [How-to guides](./TUTORIALS#-how-to-guides) - advanced guidelines for UC2 users
 * [References](./TUTORIALS#-reference-guides) - links to related topics

 Also in the TUTORIALS folder:

* [RESOURCES](./TUTORIALS/RESOURCES) of components we use
  * Find a complete shopping'n'printing list including estimated prices for all modules and setups in this [GoogleDrive Spreadsheet](https://docs.google.com/spreadsheets/d/1U1MndGKRCs0LKE5W8VGreCv9DJbQVQv7O6kgLlB6ZmE/edit?usp=sharing)
* [DATASHEETS](./TUTORIALS/DATASHEETS) of components we use

 ## [Workshop](./WORKSHOP)

 [HERE](./WORKSHOP) you find a collection of ready-to-use workshops based on the modular optics system UC2. It's in the form of documentation of the workshops we already gave.  
 The documented workshops are:

 * [In-line holography](./WORKSHOP/INLINE-HOLOGRAMM)
 * [Light sheet microscopy](./WORKSHOP/LIGHTSHEET)
 * [Comprehensive 2-day workshop](./WORKSHOP/OSLO)
 * [Short FullBOX workshop](./WORKSHOP/TiM2020)
 * [Simple Telescopes](./APPLICATIONS/APP_SIMPLE-Telescope)
 * [SimpleBOX](./TheBOX/SimpleBOX)
 * [CourseBOX](./TheBOX/CourseBOX)

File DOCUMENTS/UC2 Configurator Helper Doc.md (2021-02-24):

# UC2 Configurator Helper Doc

## Add a module to the Excel sheet

1. Add the `STL` file to the folder `CAD/RAW/STL` with the name from Inventor plus prefix `UC2_` and the suffix `_v3.stl` which means for a file named `20_Cube_Insert_CirAp_Wheel.stl` => `UC2_20_Cube_Insert_CirAp_Wheel_v3.stl`
2. Similiarily add a new folder for the module in the folder `/CAD/` with the same given in the column 2 (e.g. `ASSEMBLY_CUBE_AlliedVision_Alvium`)  

3. Open the Excel sheet and add a new module on the very left hand side which has the following structure: 

| ASSEMBLY_CUBE_AlliedVision_Alvium |                                                  |   |   |                                                                                                                           | 250,1 |
|-----------------------------------|--------------------------------------------------|---|---|---------------------------------------------------------------------------------------------------------------------------|-------|
|                                   | ASSEMBLY_CUBE_Base                               |   | 1 | Module#2                                                                                                                  | 0     |
| 250,10 €                          | 20_Cube_insert_AlliedVision_Alvium_v3            | 1 | 1 | https://github.com/bionanoimaging/UC2-GIT/blob/v3/CAD/RAW/STL/UC2_v3_20_Cube_insert_AlliedVision_Alvium_v3_1.stl          | 0,1   |
|                                   | 20_Cube_insert_AlliedVision_Alvium_adjustable_v3 | 1 | 1 | https://github.com/bionanoimaging/UC2-GIT/blob/v3/CAD/RAW/STL/UC2_v3_20_Cube_insert_AlliedVision_Alvium_adjustable_83.stl | 0,1   |
|                                   | Allied Vision Camera                             | 0 | 1 | https://www.alliedvision.com/en/digital-industrial-camera-solutions.html                                                  | 250   |

### Explanation: 

1. `ASSEMBLY_CUBE_Base` always refer to the standard base cube and will be automatically inserted by the UC2-configurator 
2. Inserts from a module e.g. `20_Cube_insert_AlliedVision_Alvium_v3` have to be inside the RAW/STL folder; it can be as many as you want
3. The running number in collum 1 is dictating the start/end point of a module
4. `Printable` if `0` it is not meant to be used for downloading; `1` refers to the STL file accordingly 
5. `Amount` gives the integer (!) number of files you want to have in one module
6. `Source` link is obsolete for printed files since the download link is generated from the Name (1)
7. `Price` is the price for the printed/bought part in €

## Add a module to an `APPLICATION`

1. Add an integer (!) number to the application in the respective column; The configurator will automatically recognize it

## Add a `Application` to the list

1. Add a new column to the end of the list with the following features:

3. `NAME`: Represents the exact folder Name of the `APPLICATION`in the folder `/APPLICATIONS` e.g. `APP_Abbe_Setup`
4. `Link to Github`: is obsolet (in future could be the image link) 
5. `Link to Image`: is obsolet (right now it takes `conver.png` or `conver.jpg` by default)
6. `Brief Description`: Write a short comment about what the application can do; It shows in the configurator (it can have HTML commands).

## Add a `BOX` to the list

Follow steps from *Add a `Application` to the list*

## Add Cover images to the Applications 

1. Place a file in `/APPLICATIONS/APP_***/IMAGES/conver.jpg`

## Remarks:

- It only works if the spelling of the filename is exactly as given by the Excel sheet! 
- If you add a new module/application/make changes to the excel sheet: you need to run the Python converter script in `/DOCUMENTS/UC2-Configurator/generate_config_from_database.py`
- The converter script will add new `config.json` files in all folders and will delete those which became obsolete
- MOVE the `END` tag to the very end such that the script recognizes the END

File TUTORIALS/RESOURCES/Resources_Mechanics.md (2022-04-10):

## Resources: Motors, Mechanics and Tools

We cannot guarantee the availability of the components. If you know other components, please let us know by filing an issue. Thank you :-)

### Motors
|  Name | Properties  |  Price | Link  | Tested |
|---|---|---|---|---|
|  28YBJ-48 | DC 5V 4 Phase 5 Wire Stepper Motor With ULN2003 Driver Board | 5€  | [Amazon](https://www.amazon.com/28YBJ-48-Stepper-ULN2003-Driver-Board/dp/B00XDTFW1M)  | Yes |
28BYJ-48 | DC 5V 4 Phase 5 Wire Stepper Motor With ULN2003 Driver Board | 6€ | [reichelt.de](https://www.reichelt.de/entwicklerboards-schrittmotor-inkl-steuerung-uln2003-debo-moto1-p192146.html) | Yes
|  XY Stage| Micro stepping motor cross platform| 4 €  | [Aliexpress](https://www.aliexpress.com/item/Micro-stepping-motor-cross-platform-small-mobile-digital-microscope-XY-axis-table-experiment-two-slide/32790147861.html)  | Yes |
Z-Focus |stepper motor micro electromagnet DIY motor driver board |3€ |[Aliexpress](https://www.aliexpress.com/i/32788292171.html?spm=a2g0x.12057483.1000001.8.2bc850e3EY8AkQ)| No

### Magnets
|  Name | Properties  |  Price | Link  | Tested |
|---|---|---|---|---|
|  Ball Magnets | 5mm, Neodym, 100 | 15€  | [Amazon](https://www.amazon.de/COFCO-125-Neodym-Kugelmagnete-5-mm/dp/B076QGPRFF/ref=sr_1_cc_5?s=aps&ie=UTF8&qid=1542899825&sr=1-5-catcorr&keywords=kugelmagnet+5mm) | Yes
|  Ball Magnets | 5mm, Neodym, 100 | 12€  | [Amazon](https://www.amazon.de/dp/B075V2G73J/?coliid=I1XQI10QI7YDJG&colid=2GSTXQZE5T6TK&psc=1&ref_=lv_vv_lig_dp_it) | No
|  Ball Magnets | 5mm, Neodym, price per piece | 0,29-0,47€  | [magnetmax.de](https://www.magnetmax.de/Neodym-Kugelmagnete/Magnetkugel-Kugelmagnet-O-5-0-mm-Neodym-vernickelt-N40-haelt-400-g::158.html) | Yes
|  Ball Magnets | 5mm, Neodym, 216 pieces | 20€ | ebay.de/itm/216-Neodym-Kugelmagnete-D5mm-D7mm-D10mm-GOLD-SILVER-BLACK-NICKEL-NdFeB/372719170845?hash=item56c7cb351d:m:mj8zDp5AN1PxzUDiyJu1Rsg | Yes
|  Ball Magnets | 5mm, Neodym, price per piece | 0,36€  | [magnetladen.de](https://www.magnetladen.de/kugelmagnet-5-mm-n42-nickel/) | Yes

### Screws
**IMPORTANT: Not all screws are magnetic!**  
It is very important to buy the right screws - the M3 screws need to attach to the magnets and therefore it is crucial that they are magnetic. STAINLESS STEEL IS GENERALLY NOT A MAGNETIC MATERIAL. THE SCREWS HAVE TO BE MADE OF GALVANIZED STEEL. If you want to know more about why not all steel is magnetic you can read about it [here](https://monnigindustry.com/2020/12/23/is-galvanized-steel-magnetic-why-or-why-not/). Unfortunately, the DIN 912 / ISO 4762 screws that we propose can be made of both and you can frequently find both at the same vendor.    
The take-home message is: **The M3 screws have be made of galvanized steel and never stainless steel!**

For people from the **US** you can purchase these "black" screws [see Discussions #83](https://github.com/openUC2/UC2-GIT/discussions/83).

|  Name | Properties  |  Price | Link  | Tested |
|---|---|---|---|---|
|  Din 912 Cylindrical | M3×8, magnetic (!), 500 pieces | 15€  | [Amazon](https://www.amazon.de/dp/B018MP15LM/ref=pe_3044161_185740101_TE_item) | Yes
|  Din 912 Cylindrical | M3×12, magnetic (!), 500 pieces | 15€  | [Amazon](https://www.amazon.de/-/en/500-12-9-ALLEN-Cylinder-Head-Screws-12-Steel/dp/B071JJ5MFW/ref=sr_1_17?dchild=1&keywords=500+st%C3%BCck+inbus+zylinderschrauben+din+912+10.9+verzinkt+m3&qid=1611568060&s=diy&sr=1-17) | Yes
Din 912 Cylindrical | M3×8, magnetic (!), 500 pieces | 15€  | [Würth](https://eshop.wuerth.de/Zylinderschraube-mit-Innensechskant-SHR-ZYL-ISO4762-88-IS25-A2K-M3X8/00843%20%208.sku/de/DE/EUR/) | Yes
Din 912 Cylindrical | M3×12, magnetic (!), 500 pieces | 15€  | [Würth](https://eshop.wuerth.de/Zylinderschraube-mit-Innensechskant-SHR-ZYL-ISO4762-88-IS25-A2K-M3X12/00843%20%2012.sku/de/DE/EUR/) | Yes
Din 912 Cylindrical | M3×18, magnetic (!), 500 pieces | 15€  | [Würth](https://eshop.wuerth.de/Zylinderschraube-mit-Innensechskant-SHR-ZYL-ISO4762-88-IS25-A2K-M3X18/00843%20%2018.sku/de/DE/EUR/) | Yes
M2/M3/M4 Kit | Stainless Steel - non-magnetic! Screws, Nuts, Bolts and Washers | 32€ | [Amazon](https://www.amazon.de/Edelstahl-Sechskopf-Knopf-Schrauben-Unterlegscheiben-Sortiment-Aufbewahrung/dp/B073SS7D8J/ref=sr_1_fkmr0_1?__mk_de_DE=%C3%85M%C3%85%C5%BD%C3%95%C3%91&keywords=zylinderkopfschrauben+set+galvanisiert&qid=1565007371&s=diy&sr=1-1-fkmr0) | Yes
Hexagon socket set screw with truncated cone | M3×25, 500 pieces  | 15€ | [Würth](https://eshop.wuerth.de/Gewindestift-Innensechskant-und-Kegelstumpf-STI-STMPF-ISO4026-45H-IS15-A2K-M3X25/025503%2025.sku/WuerthGroup-Wuerth.cgid/de/DE/EUR/?VisibleSearchTerm=STI-STMPF-ISO4026-45H-IS1%2C5-%28A2K%29-M3X25&CampaignName=SR001) | Yes
Worm screws | M3×5, magnetic, 500 pieces | 15€ | [Würth](https://eshop.wuerth.de/Gewindestift-Innensechskant-und-Kegelstumpf-STI-STMPF-ISO4026-45H-IS15-A2K-M3X5/025503%205.sku/de/DE/EUR/&SelectedFilterAttribut=%255B%257B%2522name%2522%253A%2522ATThreadTypeXNominalDiameter%2522%252C%2522value%2522%253A%255B%2522M3%2522%255D%252C%2522title%2522%253A%2522Gewindeart%2520x%2520Nenndurchmesser%2522%257D%252C%257B%2522name%2522%253A%2522ATLength%2522%252C%2522value%2522%253A%255B%25225%2520mm%2522%255D%252C%2522title%2522%253A%2522L%25C3%25A4nge%2522%257D%252C%257B%2522name%2522%253A%2522ATMaterialType%2522%252C%2522value%2522%253A%255B%2522Stahl%2522%255D%252C%2522title%2522%253A%2522Werkstoff%2522%257D%255D) | Yes
Din 912 Cylindrical | M3×8, magnetic (!), 50 pieces | 14€  | [Amazon](https://www.amazon.de/dp/B07NNSP4B5/?coliid=I1AM9O1YBO0H5Y&colid=2GSTXQZE5T6TK&psc=1&ref_=lv_vv_lig_dp_it) | No
Din 912 Cylindrical | M3×12, magnetic (!), 50 pieces | 14€  | [Amazon](https://www.amazon.de/dp/B07NP4MH15/?coliid=I2ZC4GD0H4MJN7&colid=2GSTXQZE5T6TK&ref_=lv_vv_lig_dp_it&th=1) | No
M3 nut | 100 pieces | 7€ | [Amazon](https://www.amazon.de/dp/B07FCNY726/?coliid=I36E95CHIM96IH&colid=2GSTXQZE5T6TK&psc=1&ref_=lv_vv_lig_dp_it) | No
M3×30 screw | Stainless Steel - non-magnetic! 10 pieces | 3€ | [Amazon](https://www.amazon.de/Zylinderschrauben-mit-Innensechskant-Vollgewinde-Zylinderkopfschrauben/dp/B01H9HGE4W/ref=pd_bxgy_2/261-1216229-5549766?_encoding=UTF8&pd_rd_i=B01H9HDA08&pd_rd_r=12351375-a08b-4f22-a804-5563250ddd43&pd_rd_w=LfKZk&pd_rd_wg=pTMVD&pf_rd_p=4490d326-3239-499b-8c8a-0dd8d6ad582a&pf_rd_r=TGFT2SCVQZBW7653EM5T&refRID=TGFT2SCVQZBW7653EM5T&th=1) | No
M5×8 set screw | Galvanized steel, hexagon socket, 500 pieces | 15€ | [Würth](https://eshop.wuerth.de/Produktkategorien/ISO-4026-Stahl-45H-verzinkt/14013511052004.cyid/1401.cgid/de/DE/EUR/?CatalogCategoryRef=14013511052004%40WuerthGroup-Wuerth-1401&SelectedFilterAttribut=%255B%257B%2522name%2522%253A%2522AT_ThreadTypeXNominalDiameter%2522%252C%2522value%2522%253A%255B%2522M5%2522%255D%252C%2522title%2522%253A%2522Gewindeart%2520x%2520Nenndurchmesser%2522%257D%252C%257B%2522name%2522%253A%2522AT_Length%2522%252C%2522value%2522%253A%255B%25228%2520mm%2522%255D%252C%2522title%2522%253A%2522L%25C3%25A4nge%2522%257D%255D) | Yes
Din 912 Cylindrical | M3×18, magnetic (!), 500 pieces | 15€  | [Amazon US](https://www.amazon.com/Socket-Screws-Bolts-Thread-100pcs/dp/B07CNFTK99/ref=sr_1_3?crid=RGIT53K9LFC8&keywords=100pcs%2BM3%2Bx%2B12mm%2B12.9&qid=1649551524&s=industrial&sprefix=100pcs%2Bm3%2Bx%2B12mm%2B12.9%2Cindustrial%2C109&sr=1-3&th=1

) | Yes

### Tools
|  Name | Properties  |  Price | Link  | Tested |
|---|---|---|---|---|
Bosch 603.9A8.006 IXO V Basic 3.6 | Carton Cordless Screwdriver, 100 W, 3.6 V | 45€ | [Amazon](https://www.amazon.de/Bosch-603-9A8-006-Basic-Carton-Akkuschrauber/dp/B01N43TJ8K/ref=sr_1_fkmrnull_1?__mk_de_DE=%C3%85M%C3%85%C5%BD%C3%95%C3%91&keywords=Bosch+603.9A8.006+IXO+V+Basic+3%2C6+Carton+Akkuschrauber%2C+100+W%2C+3.6+V&qid=1555592159&s=gateway&sr=8-1-fkmrnull) | Yes
Box for FullBOX | 395 x 295 x 106 mm | 13€ | [online-werkzeughandel.de](https://www.online-werkzeughandel.de/diverses/4/kunststoffkoffer-grau-b-395xh-295xt-106mm-m-schaumstoffeinlage-pp_12089_8276) | Yes

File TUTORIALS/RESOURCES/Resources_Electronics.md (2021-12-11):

## Resources: Electronics, Cameras

We cannot guarantee the availability of the components. If you know other components, please let us know by filing an issue. Thank you :-)

### ESP32
|  Name | Properties  |  Price | Link  | Tested |
|---|---|---|---|---|
|  ESP32 | Microcontroller, WiFi, Bluetooth | €  | [ESP](http://esp32.net/) | Yes |
ESP32 | Microcontroller, WiFi, Bluetooth | 10€  | [Amazon](https://www.amazon.de/AZDelivery-NodeMCU-Development-Nachfolgermodell-ESP8266/dp/B074RGW2VQ/ref=sr_1_3?__mk_de_DE=%C3%85M%C3%85%C5%BD%C3%95%C3%91&keywords=esp32&qid=1565008313&s=gateway&sr=8-3) | Yes
ESP32 | Microcontroller, WiFi, Bluetooth | 11€  | [AZ delivery](https://www.az-delivery.de/products/esp32-developmentboard?ls=de) | Yes
Wemos MINI D1 Board | ESP32 WIFI + Bluetooth | 6€ | [Ebay](https://www.ebay.de/i/162736953138?chn=ps&norover=1&mkevt=1&mkrid=707-134425-41852-0&mkcid=2&itemid=162736953138&targetid=528583141141&device=c&mktype=pla&googleloc=9042960&poi=&campaignid=1669295905&mkgroupid=63847510759&rlsatarget=pla-528583141141&abcId=1139676&merchantid=138405830&gclid=CjwKCAjwnMTqBRAzEiwAEF3ndp6IaQlxOoSLDsWtzuWXZr-Lv3IWHD-7WBUbbMnrQ8UvaPlJHiPENBoCGG8QAvD_BwE) | Yes
Wemos MINI D1 Board | ESP32 WIFI + Bluetooth | 10€ | [Eckstein](https://eckstein-shop.de/WeMos-D1-mini-Pro-WiFi-Board-ESP8266-NodeMcu-CP2104-mit-IPEX-Stecker) | No

### Arduino  
|  Name | Properties  |  Price | Link  | Tested |
|---|---|---|---|---|
|  Arduino Nano | Microcontroller | 1€  | [Arduino](http://arduino.org/)  | Yes |
Arduino Nano | Microcontroller, 5 pcs | 22€  | [Amazon](https://www.amazon.de/Anpro-Entwicklerboard-Atmega328P-Arduino-EINWEG/dp/B07H2VT2JN/ref=sr_1_1_sspa?__mk_de_DE=%C3%85M%C3%85%C5%BD%C3%95%C3%91&keywords=arduino+nano&qid=1565008279&s=gateway&sr=8-1-spons&psc=1) |
Arduino Nano | Microcontroller | 7€  | [AZ delivery](https://www.az-delivery.de/products/nano-v3-mit-ch340-arduino-kompatibel?ls=de) | No

### Raspberry Pi  
|  Name | Properties  |  Price | Link  | Tested |
|---|---|---|---|---|
|  Raspberry Pi v3b | Micro Computer, WiFi, Bluetooth, Raspbian | 25€  | [RasPi](http://raspberrpi.ort/)  | Yes |
Replacement Cable for Raspi Camera | 100 cm | 2-5€ | [Amazon](https://www.amazon.de/gp/product/B075JN61S7/ref=ox_sc_act_title_2?smid=A1X7QLRQH87QA3&psc=1) |Yes
Replacement Cable for Raspi Camera | 100 cm | 5€ | [AZ delivery](https://www.az-delivery.de/collections/raspberry-pi-kamera-zubehor/products/100cmflexkabel?ls=de) | Yes
Raspberry Pi 7" Display || 70€ | [Amazon](https://www.amazon.de/Raspberry-Pi-7-Inch-Screen-Display/dp/B014WKCFR4/ref=sr_1_fkmrnull_3?__mk_de_DE=%C3%85M%C3%85%C5%BD%C3%95%C3%91&keywords=raspi+7%22+tft&qid=1555581857&s=gateway&sr=8-3-fkmrnull) | Yes
Raspberry Pi 7" Display || 55€ | [pollin.de](https://www.pollin.de/p/raspberry-pi-tft-lc-display-7-17-78-cm-1024x600-hdmi-vga-av-121566?utm_source=geizhals.de&utm_medium=pvgl&campaign=pvgl/geizhals.de&channelid=psm&channelid/PVGL/geizhals.de) | Yes
Raspberry Pi 7" Display || 72€ |[Rasppishop](https://www.rasppishop.de/Raspberry-Pi-7-Touchscreen-Display) | Yes
Raspberry Pi 7" Display || 65€ |[reichelt.de](https://www.reichelt.de/raspberry-pi-shield-display-lcd-touch-7-800x480-pixel-raspberry-pi-7td-p159859.html?) | Yes
Raspberry Pi Case | Pi 4 & 7" Touch-Display | 23€ | [reichelt.de](https://www.reichelt.de/gehaeuse-fuer-raspberry-pi-4-7-touch-display-rpi4-case-lcd7bk-p268976.html?&trstct=pol_57) | Yes
Raspi 3 Power supply | microUSB | 12€ | [pollin.de](https://www.pollin.de/p/raspberry-pi-netzteil-t5875dv-810799) | Yes
Raspi 4 Power supply | USB-C | 10€ | [reichelt.de](https://www.reichelt.de/raspberry-pi-netzteil-5-1-v-3-0-a-usb-type-c-eu-stecker-s-rpi-ps-15w-bk-eu-p260010.html?&trstct=lsbght_sldr::259919) | Yes
Raspberry Pi 4 B | 4x 1,5 GHz, 2 GB RAM, WLAN, BT | 40€ | [reichelt.de](https://www.reichelt.de/raspberry-pi-4-b-4x-1-5-ghz-2-gb-ram-wlan-bt-rasp-pi-4-b-2gb-p259919.html?PROVID=2788&gclid=Cj0KCQjwv8nqBRDGARIsAHfR9wDfSTnmSNyUOfEQFSt3AH1NsNxiCz0buRYcON7xUyqIMCWoCNkDb1AaAl7kEALw_wcB&&r=1) | Yes

### Cameras
|  Name | Properties  |  Price | Link  | Tested |
|---|---|---|---|---|
|  Ximea | Very Small Camera | ?€  | [Ximea](https://www.ximea.com/en/products/subminiature-usb-cameras-5mpix-or-18-mpix/smallest-usb-camera-18-mpix-color-onsemi-ar1820hs)  | No |
|  Allied Vision | Monochrome Camera, CSI-2 Port or USB3 | ca. 270€  | [Allied Vision](https://www.alliedvision.com/en/products/embedded-vision-cameras/detail/Alvium/1800%20U-158.html)  | No |
Raspberry Pi Camera | NoIR V2.1 8MP 1080P | 27€ | [Amazon](https://www.amazon.de/Raspberry-Pi-v2-1-1080P-Kamera-Modul/dp/B01ER2SMHY/ref=sr_1_4?__mk_de_DE=%C3%85M%C3%85%C5%BD%C3%95%C3%91&crid=1LUZK9XHFS5CX&keywords=raspberry+pi+camera+v2.1&qid=1565008837&s=gateway&sprefix=raspberry+pi+camera+%2Caps%2C163&sr=8-4) | Yes
Raspberry Pi Camera | 8MP, IR, v2, IMX219PQ | 30€ | [reichelt.de](https://www.reichelt.de/raspberry-pi-kamera-8mp-ir-v2-imx219pq-rasp-can-2-p170857.html?&trstct=pos_2) | Yes
Daheng Imaging | IMX174 | 500€ | [https://www.get-cameras.com/](https://www.get-cameras.com/) | Yes
Astronomy camera (cooled + python interface) | IMX182| 790€ | [http://www.touptek.com/](http://www.touptek.com/) | No

### Cables and co
|  Name | Properties  |  Price | Link  | Tested |
|---|---|---|---|---|
Jumper Wires | male-to-male, 65 pcs | 4€ | [pollin.de](https://www.pollin.de/p/steckbruecken-sortiment-65-teilig-511007) | Yes
Jumper Wires | female-to-female, 40 pcs | 4€ | [Amazon](https://www.amazon.de/AZDelivery-NodeMCU-Development-Nachfolgermodell-ESP8266/dp/B074RGW2VQ/ref=sr_1_3?__mk_de_DE=%C3%85M%C3%85%C5%BD%C3%95%C3%91&keywords=esp32&qid=1565008313&s=gateway&sr=8-3) | Yes
Wires | Original Danube Cable Copper Set of 10 | 12€ | [Amazon](https://www.amazon.de/Donau-Elektronik-GMBH-Original-Kupfer/dp/B01BI1G88C/ref=sr_1_6?__mk_de_DE=%C3%85M%C3%85%C5%BD%C3%95%C3%91&keywords=kabel+set+0%2C14&qid=1565690819&s=gateway&sr=8-6) | Yes
USB-C cables | USB 2.0, USB-C, 1m, 1,5m and 2m | 8€ | [Amazon](https://www.amazon.de/Gritin-Datenkabel-Geflochtene-Robust-Daten%C3%BCbertragung-Grau/dp/B07CJJHVKX/ref=sr_1_3?keywords=usb+c+kabel&qid=1566029225&s=gateway&sr=8-3) | Yes
microUSB cables | USB 2.0, microUSB, 1m, 1,5m and 2m | 8€ | [Amazon](https://www.amazon.de/dp/B0778FV6K4/ref=sr_1_2?dchild=1&fst=as%3Aoff&qid=1586361990&refinements=p_89%3AGritin&rnid=669059031&s=computers&sr=1-2) | Yes
USB hub | USB 3.0, 4 ports (output); 1 port (input) | 12€ | [Amazon](https://www.amazon.de/Sabrent-USB-HUB-einzelnen-Schalter/dp/B00JX1ZS5O/ref=sr_1_15?__mk_de_DE=%C3%85M%C3%85%C5%BD%C3%95%C3%91&keywords=usb+hub+power&qid=1573648723&sr=8-15) | Yes

### Random Stuff
|  Name | Properties  |  Price | Link  | Tested |
|---|---|---|---|---|
Keyboard | Logitech K400 Plus 2.4 GHz Deutsch (wireless) | 25€ | [Mindfactory.de](https://www.mindfactory.de/product_info.php/Logitech-K400-Plus-2-4-GHz-Deutsch-schwarz--kabellos-_1015267.html) | Yes
Keyboard | Logitech K400 Plus 2.4 GHz Deutsch (wireless) | 27€ | [Amazon](https://www.amazon.de/Logitech-Wireless-Tastatur-deutsches-Tastaturlayout/dp/B00VHHWOU4/ref=sr_1_4?__mk_de_DE=%C3%85M%C3%85%C5%BD%C3%95%C3%91&keywords=logitech+tastatur+trackpad&qid=1565691047&s=computers&sr=1-4) | Yes
Keyboard | Logitech K400 Plus 2.4 GHz Deutsch (wireless) | 27€ | [reichelt.de](https://www.reichelt.de/funk-tastatur-usb-schwarz-touchpad-logitech-k400-p162726.html?&trstct=pos_0) | Yes
Transistor npn | BD809 80V 10A 90W TO220 | 1€ | [Ebay](https://www.ebay.de/itm/BD809-Transistor-npn-80V-10A-90W-TO220/360661360188?hash=item53f9179e3c:g:ssEAAOSw-fNaqt1l) | Yes
Transistor npn | BD809 80V 10A 90W TO220 | 0,50€ | [reichelt.de](https://www.reichelt.de/index.html?ACTION=446&LA=446&q=bd809%20transistor%20npn%2080v%2010a%2090w%20to220) | Yes
SanDisk Ultra microSD card | 64GB | 12€ | [Amazon](https://www.amazon.de/SanDisk-SDSQUAR-064G-GN6MA-microSDXC-Speicherkarte-Adapter/dp/B073JYVKNX/ref=sr_1_2?__mk_de_DE=%C3%85M%C3%85%C5%BD%C3%95%C3%91&keywords=sd+card+64+gb&qid=1565691023&s=computers&sr=1-2) | Yes

### Maker Equipment 
|  Name | Properties  |  Price | Link  | Tested |
|---|---|---|---|---|
All things you need for robots, motors, manipulation | Motion control | 1-100€ | [robotdigg](https://www.robotdigg.com/category/32/Extrusion-n-Injection) | No

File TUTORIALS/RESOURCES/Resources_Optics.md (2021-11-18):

## Resources: Optics

We cannot guarantee the availability of the components. If you know other components, please let us know by filing an issue. Thank you :-)

### Objective Lenses
|  Name | Properties  |  Price | Link  | Tested |
|---|---|---|---|---|
|  Amscope | 10x, NA=.25, TL=160mm  | 35€  | [Amazon](https://www.amazon.de/amscope-Plan-Achromatisches-Objektiv-ger%C3%A4ndelten/dp/B01G4CCB8G/ref=sr_1_6?ie=UTF8&qid=1542893150&sr=8-6&keywords=amscope+10+x+objektiv)  | Yes |
|  Optika | 20x, NA=0.40, infinity, N-plan, POL  | 95€  | [Optics-Pro](https://www.optics-pro.com/for-microscopes/optika-objective-20x-0-40-infinity-n-plan-pol-b-383pol-m-146p/p,56893)  | Yes |
|  Müller | Plan 100x, NA= 1.25 oil, TL=160, Correction=0.17 | 65€  | [Benad24](https://www.benad24.de/business-industrie/produktions-industriebedarf/medizin-labor-laborgeraete/mueller-objektiv-plan-100-1-25-oel-160-0-17-fuer-biologisches-mikroskop/a-1234576610/)  | Yes |
|  Unknown | Finite corrected, 4X 10X 20X 40X 60X 100X Achromatic Objective  | 10-135€  | [Aliexpress](https://www.aliexpress.com/item/1-set-4X-10X-20X-40X-60X-100X-Biological-Microscope-Objectives-Achromatic-lens-Free-shipping/32651361216.html?spm=2114.search0104.3.2.75af66d5taUTYa&ws_ab_test=searchweb0_0,searchweb201602_2_10065_10068_10130_5734615_10890_5730315_10547_10546_319_10548_317_5734813_10545_10696_5734713_10924_453_10084_454_10083_10618_10920_5729215_10921_10922_10307_537_536_10059_10884_10887_10928_100031_321_322_10103_5734515-5734615,searchweb201603_51,ppcSwitch_0&algo_expid=fc1adc20-26ab-43ce-b980-de2409614405-0&algo_pvid=fc1adc20-26ab-43ce-b980-de2409614405)  | Yes |
|Unknown | Finite corrected, 4X 10X 20X 40X 60X 100X Achromatic Objective|10-60€|[Aliexpress](https://de.aliexpress.com/item/32947647522.html?spm=a2g0x.search0104.3.54.6cf57a4c3DwsTO&transAbTest=ae803_3&ws_ab_test=searchweb0_0%2Csearchweb201602_6_10065_10130_10068_10890_10547_319_10546_317_10548_10545_10696_10084_453_454_10083_10618_10307_537_536_10902_10059_10884_10887_321_322_10103%2Csearchweb201603_6%2CppcSwitch_0&algo_pvid=06d972be-b176-4446-8665-56d9e61a8d2c&algo_expid=06d972be-b176-4446-8665-56d9e61a8d2c-7)|Yes
|  Unknown | Infinity corrected, 4X 10X 20X 40X 60X 100X Achromatic Objective  | 10-135€  | [Aliexpress](https://www.aliexpress.com/item/Professional-Full-Set-4X-10X-40X-100X-Achromatic-Plan-Infinity-Objective-Lens-195mm-Biological-Microscope-Objective/32837671031.html?spm=2114.search0104.3.2.570c678ewq3tmI&ws_ab_test=searchweb0_0,searchweb201602_2_10065_10068_10130_5734615_10890_5730315_10547_10546_319_10548_317_5734813_10545_10696_5734713_10924_453_10084_454_10083_10618_10920_5729215_10921_10922_10307_537_536_10059_10884_10887_10928_100031_321_322_10103_5734515,searchweb201603_51,ppcSwitch_0&algo_expid=fa024651-2d77-4fad-867c-8cd8bcf06f4c-0&algo_pvid=fa024651-2d77-4fad-867c-8cd8bcf06f4cde2409614405)  | No |
|  South Optics | Infinity corrected, 4X 10X 20X 40X 60X 100X Achromatic Objective  | 10-135€  | [South Optics](http://www.southoptics.com/website/wbsAction_loadPages.action?ssid=59&pssid=29%3E)  | No |
|  Motic | Motic Objective CCIS plan achromat. EC-H PL 4x/0.1 (AA=15.9mm)  | 101€  | [Astro Media](https://www.astroshop.de/fuer-mikroskope/motic-objektiv-ccis-plan-achromat-ec-h-pl-4x-0-1-aa-15-9mm-/p,45939)  | No |
|  Motic |Motic Achromat. Condenser N.A. 0,90/0.13 with iris  | 150€  | [Astro Media](https://www.astroshop.de/kondensoren/motic-achromat-klapp-kondensor-n-a-0-90-0-13-mit-irisblende/p,51901)  | No |
|  Various | Various | n.a. €  | [Microscopy.com](https://www.microscope.com/accessories/objective-lenses)  | No |
|  Comar | Various | n.a. €  | [Comar optics](https://www.comaroptics.com/components/lenses/mounted-lenses/microscope-objectives)  | No |
Kern Optics OBB-A1280 | Microscope Objective 4×/0,1 | 54€ | [conrad.de](https://www.conrad.de/de/p/kern-optics-obb-a1280-mikroskop-objektiv-4-x-passend-fuer-marke-mikroskope-kern-1320594.html) | Yes
Kern Optics OBB-A1108 | Microscope Objective 10×/0,3 | 40€ | [conrad.de](https://www.conrad.de/de/p/kern-optics-obb-a1108-mikroskop-objektiv-10-x-passend-fuer-marke-mikroskope-kern-1320473.html) | Yes
Cellphone Lenses | Can be used for microscpic objective lenses  | 4€ | [Megapixellenses](https://www.megapixellenses.com/) | Yes
View Solutions Microscopy parts | Microscope Objective a kinds of low-cost obejctives (long working distances!) | 40-1000€ | [View Solutions](https://viewsolutionsinc.com/microscope-parts-accessories/objective/) | Yes

Most Objectives come with an RMS thread.

We highly recommend you to check the marketing with known retailers (e.g. eBay, Amazon, Aliexpress, Alibaba). We made good experience with the low-cost optics!

### Eyepieces
|  Name | Properties  |  Price | Link  | Tested |
|---|---|---|---|---|
Kern Optics OZB-A4104 | Microscope Eyepiece 20× | 30€ | [conrad.de](https://www.conrad.de/de/p/kern-optics-ozb-a4104-mikroskop-okular-20-x-passend-fuer-marke-mikroskope-kern-1320921.html) | Yes
Unknown | Microscope Eyepiece 20×, sold in pairs | 26€ | [Aliexpress](https://de.aliexpress.com/item/32965050204.html?spm=a2g0o.productlist.0.0.7aa657eeefLUfu&algo_pvid=cd60fca0-3fa5-4191-9ce9-303815e2afa7&algo_expid=cd60fca0-3fa5-4191-9ce9-303815e2afa7-1&btsid=76036b58-6717-4d1f-a4a0-c3d4bacd0450&ws_ab_test=searchweb0_0,searchweb201602_2,searchweb201603_52) | Yes

### Lenses
Lenses are in general a troubled topic, even for us and we're constantly looking for sources of good but cheap lenses that fit our requirements. In German university environment, we mostly order from Optikbaukasten, Astromedia and of course Thorlabs. Recently we found a Canadian company Ajax Scientific, which has a very good offer but the shipping is a bit of a problem there. You can of course use any whatsoever lens that you have at hand or find at Ebay or Amazon, you can print a holder from the Lens holder on [Thingiverse](https://www.thingiverse.com/thing:4377691) - you open the part in Customiser, enter the diameter, edge thickness and focal length value and generate an STL for your lens. Make sure to use the right focal length for your experiment.

|  Name | Properties  |  Price | Link  |
|---|---|---|---|
| Convex  |  Various |  1-10 € | [Optik Baukasten](http://optik-baukasten.de/)  |
| Concave |   Various  |  1-10 € |  [Optik Baukasten](http://optik-baukasten.de/) |
| Generic  |  Various |  10-30 € | [Thorlabs](https://www.thorlabs.com/newgrouppage9.cfm?objectgroup_id=4847)  |
| Generic  |  Achromatic (Examplary) |  10-30 € | [Aliexpress](https://www.aliexpress.com/item/Diameter-25-4MM-Focal-Length-75-MM-Visible-Achromatic-Double-Lenses/32639546486.html?spm=2114.search0104.3.14.18c63065jIMhZ2&ws_ab_test=searchweb0_0,searchweb201602_3_10065_10068_10130_10890_10547_319_10546_317_10548_10545_10696_453_10084_454_10083_433_10618_431_10307_537_536_10902_10059_10884_10887_100031_321_322_10103,searchweb201603_6,ppcSwitch_0&algo_expid=3a529ed2-2a9f-4b0c-a5a1-94621e27e468-2&algo_pvid=3a529ed2-2a9f-4b0c-a5a1-94621e27e468&transAbTest=ae803_3)|
| Generic  |  Various (They used to have a large variety) |  10-30 € | [Astromedia](https://www.astroshop.de/?q=achromat)
| Generic  |  Various (They used to have a large variety) |  10-30 € |  [Edunikum](https://www.edunikum.de/sehen-licht-und-farbe/glaslinsen/)
| Generic  |  Achromatic (Examplary) |  10-30 € | [Ebay](https://www.ebay.de/itm/2pcs-Optiche-Glas-Optik-vergroserungsglas-Doublet-Achromatische-Bikonvex-Linse/172633857864?hash=item2831c79f48:m:mb2CJPQUTT-XAcOtMdZpRpw:rk:4:pf:0)
| Generic  |  Biconvex (Examplary) |  8 € | [Amazon](https://www.amazon.de/UEETEK-Brennweite-Durchmesser-Optische-Glaslinse/dp/B077N8YTGG/ref=sr_1_1?ie=UTF8&qid=1548691473&sr=8-1&keywords=Konkave+Linsen)
| Generic  |  Concave (Examplary) |  5 € | [Amazon](https://www.amazon.de/Blesiya-Physisches-Laborbedarf-Wissenschaft-Experiment/dp/B07GJW6J83/ref=sr_1_6?ie=UTF8&qid=1548691473&sr=8-6&keywords=Konkave+Linsen)
| Generic  |  Achromatic (Examplary) |  20 € | [Amazon](https://www.amazon.de/Durchmesser-Brennweite-95-K9-plano-concave-Objektiv-konkaver/dp/B013SN312E/ref=sr_1_17_sspa?ie=UTF8&qid=1548691550&sr=8-17-spons&keywords=Konkave+Linsen&psc=1)
| Generic  |  Various (Examplary) |  20 € | [Amazon - Ajax Scientific Shop](https://www.amazon.de/s/ref=bl_dp_s_web_0?ie=UTF8&search-alias=aps&field-keywords=Ajax+Scientific)
| Generic  |  Cylindrical, Plano-optics (Examplary) |  20 € | [Comar Optics](https://www.comaroptics.com/components/lenses/cylindrical-lenses/quality-planoconvex-cylindrical-lenses-visibleuv)
63 YQ 40 | cylindrical, planoconvex, f'=63mm, 40×25×4 mm, used in light sheet setup | 60€ | [Comar Optics](https://www.comaroptics.com/components/lenses/cylindrical-lenses/quality-planoconvex-cylindrical-lenses-visibleuv#row-63_yq_40)
Artikel: 2120 | planoconvex, f'=40mm, 1 inch, used in BOXes, telescopes, projector | 6€ | [Optik Baukasten](http://optik-baukasten.de/)
Artikel: 2004 | planoconvex, f'=100mm, 1 inch, used in BOXes, telescopes | 6€ | [Optik Baukasten](http://optik-baukasten.de/)
550.OA50 | achromat, f'=99,6mm, 26 mm, alternative to line above | 5€ | [Astromedia](https://www.pgi-versand.de/?id=47&mode=artdet&artnr=550.OA50)
551.OAL | achromat, f'=26,5mm, 18 mm, used in beam expander | 5€ | [Astromedia](https://www.pgi-versand.de/?id=47&mode=artdet&artnr=551.OAL)
LC1259 | planoconcave, f'=-50mm, 25 mm, used in SimpleBOX, telescopes | 19€ | [Thorlabs](https://www.thorlabs.com/thorproduct.cfm?partnumber=LC1259)
| Positive/Negative  |  Plastic and Glass lenses |  5-10 € | [Astromedia](https://www.pgi-versand.de/?id=47&mode=artlist&kat=69)
smartphone camera Lens |iPhone 5 | 5€ | [Ebay](https://www.ebay.com/itm/For-iPhone-5-Back-Camera-Replacement-Rear-Facing-Camera-With-Flash-LED/271905852188?hash=item3f4eda0b1c:g:NzYAAOSwa39UuBni)
| Generic | Bi-convex | 1-9€ | [Ajax Scientific](https://ajaxscientific.com/product/bi-convex-lens/?attribute_pa_diameter=38mm&attribute_pa_focal-length=05cm) |
| Generic | Bi-concave | 1-3€ | [Ajax Scientific](https://ajaxscientific.com/product/bi-concave-lens/?attribute_pa_diameter=38mm&attribute_pa_focal-length=05cm) |
| Bi-concave, f = -50 mm | Ajax lenses from Amazon | 10€ | [Amazon](https://www.amazon.de/-/en/Scientific-LI140-0050-Polished-Spherical-Concave-Diameter/dp/B00EPQ8ZH0) |
| Bi-convex, f = 50 mm | Ajax lenses from Amazon | 10€ | [Amazon](https://www.amazon.com/Ajax-Scientific-Double-Convex-Bi-Convex-Spherical/dp/B00EPQ9EVQ) |
| Bi-convex, f = 100 mm | Ajax lenses from Amazon | 10€ | [Amazon](https://www.amazon.com/Ajax-Scientific-Polished-Spherical-Bi-convex/dp/B00EPQ9GRS) |

### Mirrors and Others
|  Name | Properties  |  Price | Link  |
|---|---|---|---|
| Prisms/Beamsplitters  |  Various |  10-30 € | [Optik Baukasten](http://optik-baukasten.de/)  |
| Mirrors | 1 inch Mirrors to replace Thorlabs parts |  5-10 € | [Aliexpress](https://www.aliexpress.com/item/3Pcs-Free-Shipping-Mo-Reflective-Mirror-Dia-25mm-Molybdenum-Reflector-Lens-For-CO2-Laser-Cutting-Engraving/32759696170.html?spm=2114.search0104.3.2.167975efSJYug2&ws_ab_test=searchweb0_0,searchweb201602_2_10065_10068_10130_5734615_10890_5730315_10547_10546_319_10548_317_5734813_10545_10696_5734713_10924_453_10084_454_10083_10618_10920_5729215_10921_10922_10307_537_536_10059_10884_10887_10928_100031_321_322_10103_5734515,searchweb201603_51,ppcSwitch_0&algo_expid=5f5516e3-337b-4ea3-9625-bb82c9a6c350-0&algo_pvid=5f5516e3-337b-4ea3-9625-bb82c9a6c350)  |
| Grating (Transmission) |  1000 l/mm |  5 € | [Astro Media](https://experimentis-shop.de/beugungsgitter-fuer-optische-versuche-detail-441.html)  |
| Prism |  Generic |  10 € | [Amazon](https://www.amazon.de/dp/B0716T8KS4/ref=sspa_dk_detail_2?psc=1&pd_rd_i=B0716T8KS4&pd_rd_w=LKu5R&pf_rd_p=00903874-3af0-47e0-8622-ee58087f71cf&pd_rd_wg=SNXHK&pf_rd_r=WXGT2NAAVMTR9QDASTY2&pd_rd_r=8b223bf8-2316-11e9-bb57-2164ec7a06dc)  |
| Dichroic Prism/BS |  Generic |  10 € | [Amazon](https://www.amazon.de/Askliy-Physik-Pr%C3%A4zision-optisch-Prisma/dp/B01LSATQI2/ref=pd_bxgy_328_img_2?_encoding=UTF8&pd_rd_i=B01LSATQI2&pd_rd_r=eadee6fe-2316-11e9-9f91-fdda01699348&pd_rd_w=4rz9k&pd_rd_wg=wDsca&pf_rd_p=c63cca93-7a15-40dd-b68a-47167d2b2080&pf_rd_r=RMDXQTSY6WHWMVE03SGS&psc=1&refRID=RMDXQTSY6WHWMVE03SGS)  |
| Silver Mirror |  Generic |  45 € | [Eksma](http://eksmaoptics.com/femtoline-components/femtoline-mirrors/enhanced-silver-mirrors/?listtype=search&searchparam=mirror)  |
| Microlens Arrays |  Generic |  450 € | [RPC Photonics](https://www.rpcphotonics.com/product-category/microlens-arrays/) |
Protected Silver Mirror | 1 inch, PF10-03-P01 | 50€ | [Thorlabs](https://www.thorlabs.com/thorproduct.cfm?partnumber=PF10-03-P01)
Mirrors | 30×30 mm², sticker, package of 45 pcs | 4€ | [Amazon](https://www.amazon.de/Rayher-14548606-Spiegelmosaik-selbstklebend-SB-Btl/dp/B008KJ8438/ref=pd_bxgy_201_img_3/258-8761405-4543762?_encoding=UTF8&pd_rd_i=B008KJ8438&pd_rd_r=80fd534c-997b-4a19-b91a-9bf38dbf4ade&pd_rd_w=4DEXV&pd_rd_wg=7SLRE&pf_rd_p=98c98f04-e797-4e4b-a352-48f7266a41af&pf_rd_r=N95R9S45MNSYNQX2BAJE&psc=1&refRID=N95R9S45MNSYNQX2BAJE)
Mirrors | 30×30 mm², sticker, package of 45 pcs | 4€ | [Rayher](https://www.rayher.com/de/spiegelmosaik-selbstklebend-14548606)
| Quarter Wave Plates | knight optical | 20-50 € | [Knight Optical](https://www.knightoptical.com/stock/optical-components/uvvisnir-optics/retarders/plastic-retarders/) |

### Filters
|  Name | Properties  |  Price | Link  |
|---|---|---|---|
| Fluorescent Filters  |  Various |  10-30 € | [Comar Filters](https://www.comaroptics.com/components/filters/)  |
| Dichroics  |  Various |  10-30 € | [Comar Filters](https://www.comaroptics.com/components/filters/)  |
| Long-/Band-pass filters  |  Various |  10-30 € | [Comar Filters](https://www.comaroptics.com/components/filters/)  |
| Rosco Gel Filters |   Various |  10-30 € | [RoscoLux Filters](http://www.rosco.com/filters/roscolux.cfm)  |
Lee filters | #010 medium yellow works for the 445nm laser pointer | | [Lee filters](http://www.leefilters.com/lighting/colour-details.html#010&filter=cf)
Polarizing filters | |11€ |[Aliexpress](https://www.aliexpress.com/item/32809585908.html?spm=2114.search0104.3.2.40184d9dlpQh36&ws_ab_test=searchweb0_0,searchweb201602_6_10065_10130_10068_10890_10547_319_10546_317_10548_10545_10696_453_10084_454_10083_10618_10307_537_536_10059_10884_10887_321_322_10103,searchweb201603_6,ppcSwitch_0&algo_expid=99e4204e-1391-4a93-875f-803f0fe4ca13-0&algo_pvid=99e4204e-1391-4a93-875f-803f0fe4ca13&transAbTest=ae803_3)

A set of excellent resources for proper low-cost filter selection can be found here:

Gel-Filters (mostly from Roscolux):
[Kurt Thorn' Blog](http://nic.ucsf.edu/blog/2013/10/theatrical-gels-as-color-filters/)

Gel-Filters Case scenario [Wormlab](http://post.queensu.ca/~chinsang/lab-protocols/gfp-stereoscope.html)

[GFP (with # for ordering the parts):](https://makezine.com/2011/03/04/cheap-diy-gfp-green-fluorescent-protein-illuminator/)

[Comar Interference Filters:](https://github.com/OpenLabTools/Imaging_RPi_Fluorescence/blob/master/content.md)

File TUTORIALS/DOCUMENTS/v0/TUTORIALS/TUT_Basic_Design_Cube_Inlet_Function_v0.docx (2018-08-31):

# How to design a cube’s inlet/function

V0, 31.08.2018

B. Diederich

# Introduction

The UC2 Toolbox serves as a base system which acts as the skeleton for holding dindividual functions. Each block has in its base version a edge-length of 50 mm and can be produced using off-the-shelf 3D printers. Those cubes are mounted on a grid acting as a base-plate. Fixed positioning is assured by relying on magnetic fit, where the cubes have inbuilt screws, fitting directly on the ball-magnets pressed into the base-plate.


The skeleton itself is not ready for optical experiments yet. Therefore we have to place individual functions inside the cubes (e.g. cameras, lenses, mirrors, light sources, etc.). There is a list of available inlets to realize basic experiments already. But most devices won’t follow these dimensions, which makes customized adapters necessary.

This should give a basic guide on how to design a function which fits into the UC2 cube. Basically there are two ways to mount stuff inside a cube.

1. 5mm Rod-System for use with popular Cage Systems
2. Integrated “rail”-system to slide in customized functions

# 1 – ROD-SYSTEM

We integrated the rod-system from the popular cage system available for example from Thorlabs, Edmund Optics or Qioptiq. This means, that one can put lens which are already available in the optical lab directly into the cubes without any redesigning of the parts. Problem with these rods is, that they are measured in inch not mm. Thus, Thorlabs has rods with 2inch=50,8mm not fitting into our cubes, which need <50mm to work correctly.


THORLABS CP02-M

Base CUBE

# 2 – INLET SYSTEM

Some components won’T fit intoe the Thorlabs cage system because of their footprint. Therefore we designed a sliding system which can hold basically every component, like the Raspberry’s camera for example. It is slightly bigger as distances between the rods, thus not “slidable” using the rods. The dimensions can be extracted from the CAD technical drawing below. The major importance is, that the “wings” can slide freely in the adapter, but are not too loose to loose contact. We designed a set of adapters for multiple purposes. Mirrors, camera adapters or filter mounts are just a few of them. This adapter is customizable to fit everybodies individual needs. Therefore we invite you to freely modify it to your needs and publish your results.


Raspi-Camera Adapter

Base CUBE

The shape of the inlet or the adapter which fits into the sliding system looks as follow:

## Dimensions of the inlet System

This is an example for a mirror-mount. It can be modified to your needs of course.


Slide

- Fit into Cube

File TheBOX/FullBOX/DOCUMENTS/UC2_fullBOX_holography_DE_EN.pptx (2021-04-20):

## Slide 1

Inline Holographie - Abbildung ohne Linsen

Interferenz und Beugung kann man nicht mit klass. Strahlenoptik erklären

Wellenoptik behandelt Licht wie eine elektromagnetische Welle

Lichtstrahl

Von einer Punktlichtquelle gehen kugelförmige Wellen aus.

LED

Lochblende (Pinhole)

Probe

Kamera


Hologramm eines Punktes

Wellenfront

Wellenfront

…

Interferenz – wenn Wellen sich treffen.

In weiter Entfernung von der Quelle ist eine Kugelwelle ähnlich einer ebenen Welle.


Wellenfront

Wellenfront

Hologramm der Kieselalgen?


useetoo.org

YOU
SEE,
TOO

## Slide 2

Inline Holography – Lensless Imaging

Interference and Diffreaction cannot be explained using Ray Optics

Wave Optics describes light as an electromagnetic wave

Light ray

Spherical wave propagates from a point light source.

LED

Pinhole

Sample

Camera

Hologram of a point-like object

Wave front

Wave front

…

Interference – when the waves meet each other

Far away from the light source the spherical waves look like plane waves.

Wave front

Wave front

Hologram of Diatoms?

useetoo.org

YOU
SEE,
TOO

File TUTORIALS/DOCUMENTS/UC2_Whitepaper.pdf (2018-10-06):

# Promotion Modular Optical System

UC2 by René Richter and Benedict Diederich
IPHT, Institute of Photonic Technology, Albert-Einstein-Straße 9, 07745 Jena

## Abstract / Abstract

In the present project, a modular, cost-effective, reduced-complexity, yet high-resolution microscopy system is developed. Image capture and processing devices, such as smartphones in conjunction with 3D rapid prototyping, significantly reduce production costs.
The modular design allows fast and easy adaptation of the system to the specific requirements of the end user. In combination with intelligent algorithms the use of the microscopy system for single molecule detection (dSTORM) and scanning microscopy (ISM) is also made possible.

The project presented here aims to provide high-resolution, inexpensive microscopes for the general public, educational concepts and scientific special tasks in the form of a democratization of device development. The focus is on field research, for instant microscopic diagnostics, e.g. Malaria, in the S3 laboratory as a "disposable microscope" or also for use in the educational context.

## Motivation

There are about 2.3 billion mobile phones in daily use, of which the majority have high-resolution integrated cameras. By modern image analysis techniques enable the observation


Figure 1 - Exemplary configuration of the Abbe experiment to demonstrate the effect on the optical resolution in the pupillary intervention of the quality of drinking water in remote or economically weak regions, e.g. in developing countries.
The field of "telemedicine" is one of the first in which the smartphone has long been established as a measuring instrument. In this case, the data acquisition in the field takes place directly at the user and from there, e.g. for analysis in clinics.

For some time, the trend has been towards the modularization and reusability of technical devices. Google's project Ara describes e.g. a modular smartphone concept in which the battery, CPU, camera and other components are interchangeable and thus self-configurable. project goal

The aim of the proposed project is to transfer this concept of modularization to optical superstructures, especially microscopes. For this purpose, a system in the form of an optical kit is to be developed, which can be dynamically adapted to the task of the users.
In this way, the creativity of the users should be more involved in the development of modules. The function thus no longer results at the moment of the product, but results from the sum of the variable parts in combination with the creativity of the user.

## Working Principle

The modular System relies on the well-known principle of Fourier-Optics. This is realized by the letting focal lengths of adjacent lenses follow one another. This makes it very robust to align any given optical setup. It reduces possible aberrations induced by misaligned lenses on the optical axis. Magnets and their corresponding counterparts allow an easy to use alignment system where misalignment is hardly possible. It promotes the easy of playing with different optical modalities and let users get creative.


## Exploitation

In order to clarify scientific and social relevance, some practical examples – some of which are already in the practical test phase - are shown in figure 1 and 3.

Figure 2 - Two Building Blocks and the magnetic base-plate.
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

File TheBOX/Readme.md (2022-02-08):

# The BOX
Our BOXes are still a work-in-progress - we test them, optimize them and continually improve them. The renderings on this page show the BOXes in v3 version, but you still find the documentation of their assembly and alignment relying on images of v2 cubes.

TheBOX is a number of optical experiments compiled into a ready-to-use box. We created three variants for different levels of knowledge and skills. SimpleBOX covers the basic experiments of ray optics for secondary and high schools. CourseBOX  teaches the core principles of microscopy from a simple lens to laser scanning confocal microscopy. FullBOX is meant to be used by university students and researchers for the everyday labwork or advanced
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

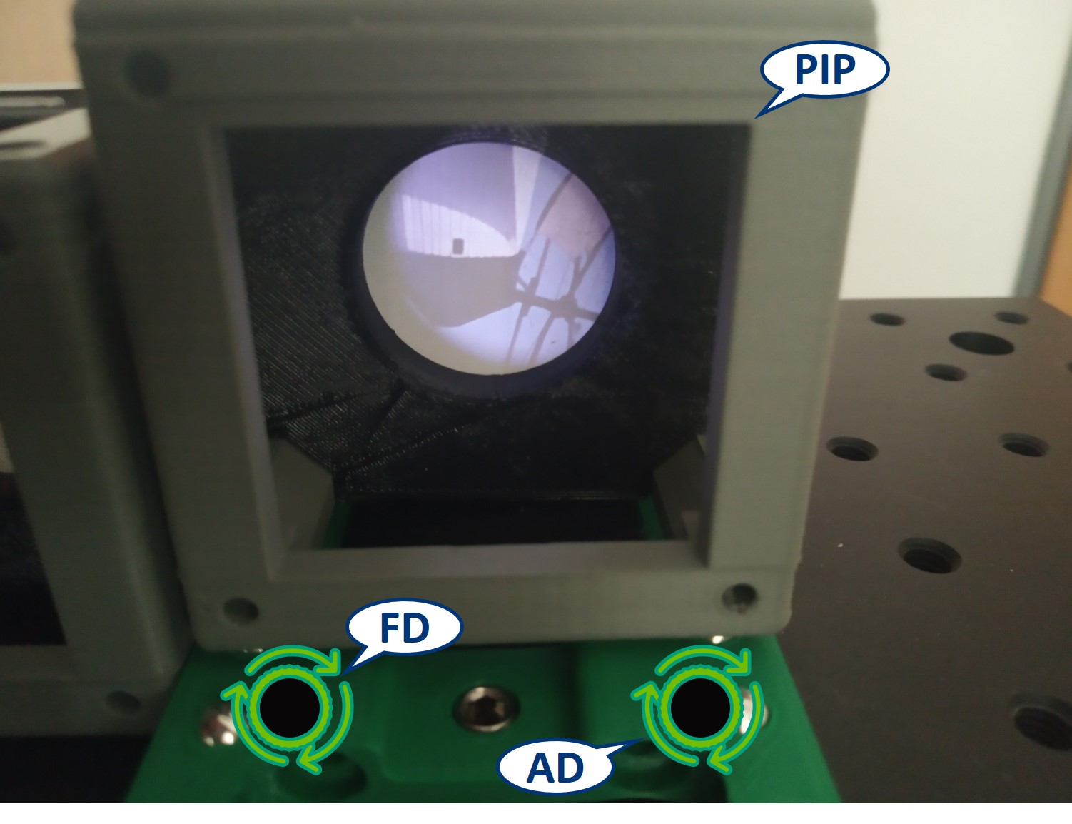
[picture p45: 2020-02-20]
TheBOX/CourseBOX/ALIGNMENT_FinOptics/IMAGES/UC2_coreBOX_alignment_33.jpg

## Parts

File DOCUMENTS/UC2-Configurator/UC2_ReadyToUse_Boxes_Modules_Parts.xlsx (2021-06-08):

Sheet: Complete overview
 |  |  |  |  |  |  | BOXes |  |  | APPLICATIONs
 |  | The overall price is an estimate. Includes only material used. Some parts may need to be purchased in larger amounts. The prices of components listed vary among different vendors. The price of 3D printing material used to calculate the price of the components is 30€/kg. |  |  |  |  | SimpleBOX | CourseBOX | FullBOX | APP_Abbe_Setup | APP_Double-slit_Experiment | APP_INLINE_HOLOGRAM (https://github.com/AlecVercruysse/UC2-GIT/tree/master/APPLICATIONS/APP_INLINE_HOLOGRAM) | APP_Incubator_Microscope (https://github.com/AlecVercruysse/UC2-GIT/tree/master/APPLICATIONS/APP_Incubator_Microscope) | APP_Incubator_Microscope_fluorescence | APP_Mach-Zehnder_Interferometer | APP_Michelson_Interferometer | APP_SIMPLE-Projector | APP_SIMPLE-Smartphone_Microscope | APP_SIMPLE-Telescope | APP_SMARTPHONE_MICROSCOPE | APP_Spectrometer
 | Link to Github |  |  |  |  |  | https://github.com/bionanoimaging/UC2-GIT/tree/master/TheBOX/SimpleBOX | https://github.com/bionanoimaging/UC2-GIT/tree/master/TheBOX/CourseBOX | https://github.com/bionanoimaging/UC2-GIT/tree/master/TheBOX/FullBOX | https://github.com/bionanoimaging/UC2-GIT/tree/master/APPLICATIONS/APP_Abbe_Setup | https://github.com/bionanoimaging/UC2-GIT/tree/master/APPLICATIONS/APP_Double-slit_Experiment | https://github.com/bionanoimaging/UC2-GIT/tree/master/APPLICATIONS/APP_INLINE_HOLOGRAM | https://github.com/bionanoimaging/UC2-GIT/tree/master/APPLICATIONS/APP_Incubator_Microscope | https://github.com/bionanoimaging/UC2-GIT/tree/master/APPLICATIONS/APP_LIGHTSHEET_Workshop | https://github.com/bionanoimaging/UC2-GIT/tree/master/APPLICATIONS/APP_Mach-Zehnder_Interferometer | https://github.com/bionanoimaging/UC2-GIT/tree/master/APPLICATIONS/APP_Michelson_Interferometer | https://github.com/bionanoimaging/UC2-GIT/tree/master/APPLICATIONS/APP_SIMPLE-Projector | https://github.com/bionanoimaging/UC2-GIT/tree/master/APPLICATIONS/APP_SIMPLE-Smartphone_Microscope/mechanical | https://github.com/bionanoimaging/UC2-GIT/tree/master/APPLICATIONS/APP_SIMPLE-Telescope | https://github.com/bionanoimaging/UC2-GIT/tree/master/APPLICATIONS/APP_SMARTPHONE_MICROSCOPE | https://github.com/bionanoimaging/UC2-GIT/tree/master/APPLICATIONS/APP_Spectrometer
 | Link to Image |  |  |  |  |  | https://github.com/bionanoimaging/UC2-GIT/blob/master/TheBOX/IMAGES/SimpleBOX.jpg?raw=true | https://github.com/bionanoimaging/UC2-GIT/blob/master/TheBOX/IMAGES/CourseBOX.jpg?raw=true | https://github.com/bionanoimaging/UC2-GIT/blob/master/TheBOX/IMAGES/FullBOX.jpg?raw=true | https://github.com/bionanoimaging/UC2-GIT/blob/master/APPLICATIONS/APP_Abbe_Setup/IMAGES/Application_Abbe-Experiment_v2.png?raw=true | https://github.com/bionanoimaging/UC2-GIT/blob/master/APPLICATIONS/APP_Double-slit_Experiment/IMAGES/UC2_Setups_13_Double-slit.png?raw=true | https://github.com/bionanoimaging/UC2-GIT/blob/master/APPLICATIONS/APP_INLINE_HOLOGRAM/IMAGES/Application_Inline_Holographic_Microscopy_v2.png?raw=true | https://github.com/bionanoimaging/UC2-GIT/blob/master/APPLICATIONS/APP_Incubator_Microscope/IMAGES/Assembly_UKJ_Microscope_v4_2.png?raw=true | https://github.com/bionanoimaging/UC2-GIT/blob/master/APPLICATIONS/APP_LIGHTSHEET_Workshop/IMAGES/Assembly_simple_Lightsheet_v1.png?raw=true | https://github.com/bionanoimaging/UC2-GIT/blob/master/APPLICATIONS/APP_Mach-Zehnder_Interferometer/IMAGES/UC2_Setups_11_mach-zehnder.png?raw=true | https://github.com/bionanoimaging/UC2-GIT/blob/master/APPLICATIONS/APP_Michelson_Interferometer/IMAGES/Application_Michelson-Interferometer_v2_2.png?raw=true | https://github.com/bionanoimaging/UC2-GIT/blob/master/APPLICATIONS/APP_SIMPLE-Projector/IMAGES/UC2_Setups_12_Projector.png?raw=true | https://github.com/bionanoimaging/UC2-GIT/blob/master/APPLICATIONS/APP_SIMPLE-Smartphone_Microscope/IMAGES/Application_simple_smartphone_microscope_v2.png?raw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 | https://github.com/bionanoimaging/UC2-GIT/blob/master/APPLICATIONS/APP_SIMPLE-Telescope/IMAGES/Assembly_simple_Telescope.png?raw=true | https://github.com/bionanoimaging/UC2-GIT/blob/master/APPLICATIONS/APP_SMARTPHONE_MICROSCOPE/IMAGES/Assembly_smartphone_microscope_2.png?raw=true | https://github.com/bionanoimaging/UC2-GIT/blob/master/APPLICATIONS/APP_Spectrometer/IMAGES/UC2_Setups_10_spectrometer.png?raw=true
 | Brief Description |  |  |  |  |  | The SimpleBOX contains only mechanical modules and covers experiment for 7th to 12th grade. | The CourseBOX is a collection of modules optimised for Optical Alignment and Microscopy courses. | The FullBOX is a comprehensive toolbox that includes both the simple and advanced experiments. | The famous Abbe Diffraction Experiment demonstartes the image formation in optical setup. | The basic interference experiment demonstartes the wave property of light. | Inline Holographic microscope creates a hologramm without using any lenses. | Incubator Microscope is using the simplest possible finite-corrected microscope scheme to image living samples in natural conditions. | The Light sheet Microscope demonstartes the principle of sellective plane illumination methods. | Mach-Zehnder Interferometer is a device used for determining the phase change, caused by the sample. | Michelson Interferometer is sensitive to surface variation of the observed sample, compared to a flat mirror. | This SIMPLE experiment shown the image formation done by a single lens. | The SIMPLE Smartphone microscope allows for imaging the sample using a Smartphone, without the need of further electronics. | The SIMPLE Telescope demostartes the principles of the most common refractvive telescopes. | The Smartphone microscope is a classical transmission microscope optimised for the use of a smartphone for imaging. | The Spectrometer uses a grating to disperse the incoming light and allows for imaging of the transmission spectrum of the sample.
# | Module | Part | Printable | Amount | Source | Price per amount | 146.81 € | 295.22 € | 618.33 € | 557.07 € | 239.47 € | 236.97 € | 314.38 € | 423.79 € | 365.52 € | 320.89 € | 26.22 € | 81.75 € | 63.44 € | 134.43 € | 284.54 €
1 | ASSEMBLY_Baseplate 4x11 |  |  |  |  | 8.22 | 3 | 4 | 2 | 0 | 1 | 1 | 0 | 0 | 1 | 0 | 1 | 0 | 2 | 0 | 0
 | https://github.com/bionanoimaging/UC2-GIT/tree/master/CAD/ASSEMBLY_Baseplate_v2 | Baseplate 4x1 | 1 | 1 | https://github.com/bionanoimaging/UC2-GIT/blob/master/CAD/ASSEMBLY_Baseplate_v2/STL/Assembly_base_4x1.stl | 0.7
 | 8.22 € | Ballmagnets | 0 | 16 | https://www.magnetmax.de/Neodym-Kugelmagnete/Magnetkugel-Kugelmagnet-O-5-0-mm-Neodym-vernickelt-N40-haelt-400-g::158.html | 0.47
2 | ASSEMBLY_Baseplate 4x2 |  |  |  |  | 16.34 | 1 | 1 | 1 | 1 | 0 | 0 | 1 | 0 | 0 | 0 | 0 | 1 | 0 | 0 | 0
 | https://github.com/bionanoimaging/UC2-GIT/tree/master/CAD/ASSEMBLY_Baseplate_v2 | Baseplate 4x2 | 1 | 1 | https://github.com/bionanoimaging/UC2-GIT/blob/master/CAD/ASSEMBLY_Baseplate_v2/STL/Assembly_base_4x2.stl | 1.3
 | 16.34 € | Ballmagnets | 0 | 32 | https://www.magnetmax.de/Neodym-Kugelmagnete/Magnetkugel-Kugelmagnet-O-5-0-mm-Neodym-vernickelt-N40-haelt-400-g::158.html | 0.47
3 | ASSEMBLY_Baseplate 4x4 |  |  |  |  | 32.68 | 0 | 0 | 1 | 1 | 0 | 0 | 0 | 1 | 1 | 1 | 0 | 0 | 0 | 1 | 1
 | https://github.com/bionanoimaging/UC2-GIT/tree/master/CAD/ASSEMBLY_Baseplate_v2 | Baseplate 4x4 | 1 | 1 | https://github.com/bionanoimaging/UC2-GIT/blob/master/CAD/ASSEMBLY_Baseplate_v2/STL/Assembly_base_4x4.stl | 2.6
 | 32.68 € | Ballmagnets | 0 | 64 | https://www.magnetmax.de/Neodym-Kugelmagnete/Magnetkugel-Kugelmagnet-O-5-0-mm-Neodym-vernickelt-N40-haelt-400-g::158.html | 0.47
4 | ASSEMBLY_CUBE_empty_1x1 |  |  |  |  | 2.2 | 0 | 0 | 0 | 0 | 0 | 0 | 0 | 0 | 0 | 0 | 0 | 3 | 0 | 3 | 0
 | https://github.com/bionanoimaging/UC2-GIT/tree/master/CAD/ASSEMBLY_CUBE_Base_v2 | 10_Cube_1x1 | 1 | 1 | https://github.com/bionanoimaging/UC2-GIT/blob/master/CAD/ASSEMBLY_CUBE_Base_v2/STL/10_Cube_1x1_v2.stl | 0.4
 | 2.20 € | 10_Lid_1x1 | 1 | 1 | https://github.com/bionanoimaging/UC2-GIT/blob/master/CAD/ASSEMBLY_CUBE_Base_v2/STL/10_Lid_1x1_v2.stl | 0.2
 |  | Screws M3x12 | 0 | 4 | https://eshop.wuerth.de/Zylinderschraube-mit-Innensechskant-SHR-ZYL-ISO4762-88-IS25-A2K-M3X12/00843%20%2012.sku/de/DE/EUR/ | 0.2
 |  | Screws M3x8 (optional) | 0 | 4 | https://eshop.wuerth.de/Zylinderschraube-mit-Innensechskant-SHR-ZYL-ISO4762-88-IS25-A2K-M3X8/00843%20%208.sku/de/DE/EUR/ | 0.2
5 | ASSEMBLY_CUBE_Beamexpander |  |  |  |  | 12.1 | 0 | 1 | 1 | 0 | 0 | 0 | 0 | 1 | 1 | 1 | 0 | 0 | 0 | 0 | 0
 | https://github.com/bionanoimaging/UC2-GIT/tree/master/CAD/ASSEMBLY_CUBE_Beamexpander_v2 | ASSEMBLY_CUBE_empty_1x1 |  | 1 | A14;E18 | 2.2
 | 12.10 € | 20_Cube_Insert_Beamexpander | 1 | 1 | https://github.com/bionanoimaging/UC2-GIT/blob/master/CAD/ASSEMBLY_CUBE_Beamexpander_v2/STL/20_Cube_Insert_Beamexpander.stl | 0.3
 | Beamexpander collimates light from a laser into a uniform beam of 20 mm diameter. | 30_Lens_Adapter_Beamexpander | 1 | 1 | https://github.com/bionanoimaging/UC2-GIT/blob/master/CAD/ASSEMBLY_CUBE_Beamexpander_v2/STL/30_Lens_Adapter_Beamexpander.stl | 0
 |  | iPhone Lens | 0 | 1 | https://www.ebay.com/c/7029261375 | 4.6
 |  | Planoconvex Lens f'=26,5mm, 18 mm (551.OAL) | 0 | 1 | https://www.pgi-versand.de/?id=47&mode=artdet&artnr=551.OAL | 5
6 | ASSEMBLY_CUBE_Beamsplitter |  |  |  |  | 29.2 | 0 | 1 | 1 | 1 | 0 | 0 | 0 | 0 | 2 | 1 | 0 | 0 | 0 | 0 | 0
 | https://github.com/bionanoimaging/UC2-GIT/tree/master/CAD/ASSEMBLY_CUBE_Beamsplitter_v2 | ASSEMBLY_CUBE_empty_1x1 |  | 1 | A14;E18 | 2.2
 | 29.20 € | 20_Cube_Insert_Beamsplitter | 1 | 1 | https://github.com/bionanoimaging/UC2-GIT/blob/master/CAD/ASSEMBLY_CUBE_Beamsplitter_v2/STL/20_Cube_Insert_Beamsplitter.stl | 0.3
 | The module hold a 50:50 glass beamsplitter. | Beamsplitter Cube (Art. 2137) | 0 | 1 | https://optikbaukasten.de/ | 26.7
7 | ASSEMBLY_CUBE_Eyepiece |  |  |  |  | 16.11 | 1 | 0 | 1 | 0 | 0 | 0 | 0 | 0 | 0 | 0 | 0 | 1 | 0 | 1 | 0
 | https://github.com/bionanoimaging/UC2-GIT/tree/master/CAD/ASSEMBLY_CUBE_Eyepiece_v2 | ASSEMBLY_CUBE_empty_1x1 |  | 1 | A14;E18 | 2.2
 | 16.11 € | 20_Cube_Insert_Holder-okular | 1 | 1 | https://github.com/bionanoimaging/UC2-GIT/blob/master/CAD/ASSEMBLY_CUBE_Eyepiece_v2/STL/20_Cube_Insert_Holder-okular_v2.stl | 0.2
 | The eyepiece is aligned to the smartphone holder, which is attached to the cube from outside. Together, they provide optimal conditions for imaging by a smartphone. | 30_Smartphone_Holder | 1 | 1 | https://github.com/bionanoimaging/UC2-GIT/blob/master/CAD/ASSEMBLY_CUBE_Eyepiece_v2/STL/30_Smartphone_Holder.stl | 0.6
 |  | Eyepiece 20x | 0 | 1 | https://de.aliexpress.com/item/32965050204.html | 13.11
8 | ASSEMBLY_CUBE_LED_Matrix |  |  |  |  | 23.69 | 0 | 0 | 1 | 0 | 0 | 0 | 1 | 0 | 0 | 0 |  | 0 | 0 | 1 | 0
 | https://github.com/bionanoimaging/UC2-GIT/tree/master/CAD/ASSEMBLY_CUBE_LED_Matrix_v2 | 10_Lid_1x1 | 1 | 1 | https://github.com/bionanoimaging/UC2-GIT/blob/master/CAD/ASSEMBLY_CUBE_LED_Matrix_v2/STL/10_Lid_1x1_el_v2.stl | 0.2
 | 23.69 € | 30_Cube_LED_Array | 1 | 1 | https://github.com/bionanoimaging/UC2-GIT/blob/master/CAD/ASSEMBLY_CUBE_LED_Matrix_v2/STL/30_Cube_LED_Array_v0.stl | 0.2
 | The 8x8 LED matrix serves as a light source for trasmission microscopy. | Screws M3x12 | 0 | 4 | https://eshop.wuerth.de/Zylinderschraube-mit-Innensechskant-SHR-ZYL-ISO4762-88-IS25-A2K-M3X12/00843%20%2012.sku/de/DE/EUR/ | 0.2
 |  | M2 screw + nut | 0 | 2 | https://www.amazon.de/Edelstahl-Sechskopf-Knopf-Schrauben-Unterlegscheiben-Sortiment-Aufbewahrung/dp/B073SS7D8J?__mk_de_DE=%C3%85M%C3%85%C5%BD%C3%95%C3%91&s=diy | 0.1
 |  | LED Matrix 8x8 | 0 | 1 | https://www.amazon.de/AZDelivery-Matrix-CJMCU-8-Arduino-Raspberry/dp/B078HYP681?__mk_de_DE=%C3%85M%C3%85%C5%BD%C3%95%C3%91&s=gateway | 9.99
 |  | ESP32 | 0 | 1 | https://www.amazon.de/AZDelivery-NodeMCU-Development-Nachfolgermodell-ESP8266/dp/B074RGW2VQ?__mk_de_DE=%C3%85M%C3%85%C5%BD%C3%95%C3%91&s=gateway | 8
 |  | Female-Female Jumper Wire | 0 | 3 | https://www.amazon.de/-/en/AZDelivery-Jumper-Arduino-Raspberry-Breadboard/dp/B07KYHBVR7 | 0.5
 |  | USB-microUSB cable | 0 | 1 | https://www.amazon.de/dp/B0778FV6K4?fst=as%3Aoff&rnid=669059031&s=computers | 2.8
9 | ASSEMBLY_CUBE_LED |  |  |  |  | 7.25 | 0 | 0 | 1 | 1 | 1 | 1 | 0 | 0 | 0 | 0 | 0 | 0 | 0 | 0 | 1
 | https://github.com/bionanoimaging/UC2-GIT/tree/master/CAD/ASSEMBLY_CUBE_LED_v2 | ASSEMBLY_CUBE_empty_1x1 |  | 1 | A14;E18 | 2.2
 | 7.25 € | 20_Cube_insert_LED_holder | 1 | 1 | https://github.com/bionanoimaging/UC2-GIT/blob/master/CAD/ASSEMBLY_CUBE_LED_v2/STL/ASSEMBLY_CUBE_LED_20_Cube_insert_LED_holder.stl | 0.2
 | The blue or ultraviolet LED serves a light source for the In-holography. When the cube is equiped with an extra sample holder, a pinhole can be mounted directly in front of LED. | 20_Cube_insert_Sample_holder (optional) | 1 | 1 | https://github.com/bionanoimaging/UC2-GIT/blob/master/CAD/ASSEMBLY_CUBE_LED_v2/STL/ASSEMBLY_CUBE_LED_20_Cube_insert_Sample_holder.stl | 0.3
 |  | 20_Cube_Insert_Sample_clamp (optional) | 1 | 1 | https://github.com/bionanoimaging/UC2-GIT/blob/master/CAD/ASSEMBLY_CUBE_LED_v2/STL/ASSEMBLY_CUBE_LED_20_Cube_Insert_Sample_clamp.stl | 0
 |  | Hi-Power LED 1W/3W UV STAR Blue | 0 | 1 | https://www.ebay.de/itm/Hi-Power-LED-1W-3W-UV-STAR-Ultraviolet-/131326525056?var= | 1.85
 |  | wire | 0 | 1 | https://www.amazon.de/Donau-Elektronik-GMBH-Original-Kupfer/dp/B01BI1G88C?__mk_de_DE=%C3%85M%C3%85%C5%BD%C3%95%C3%91&s=gateway | 0.1
 |  | Resistor | 0 | 1 |  | 0
 |  | USB-microUSB cable | 0 | 1 | https://www.amazon.de/dp/B0778FV6K4?fst=as%3Aoff&rnid=669059031&s=computers | 2.8
 |  | Wago binder | 0 | 1 | https://www.amazon.de/Sortiment-2273-202-Verbindungsklemme-praktischem-Sortimentskasten/dp/B06WLLCH5Y?__mk_de_DE=%C3%85M%C3%85%C5%BD%C3%95%C3%91&s=gateway | 0.1
10 | ASSEMBLY_CUBE_Laser |  |  |  |  | 18.4 | 0 | 1 | 1 | 0 | 0 | 0 | 0 | 1 | 1 | 1 | 0 | 0 | 0 | 0 | 0
 | https://github.com/bionanoimaging/UC2-GIT/tree/master/CAD/ASSEMBLY_CUBE_Laser_v2 | ASSEMBLY_CUBE_empty_1x1 |  | 1 | A14;E18 | 2.2
 | 18.40 € | 20_Cube_Insert_Laser_Mount | 1 | 2 | https://github.com/bionanoimaging/UC2-GIT/blob/master/CAD/ASSEMBLY_CUBE_Laser_v2/STL/20_Cube_Insert_Laser_Mount.stl | 0.3
 | The laser serves as a light source. It can be centered using four screws pushing from four sides of the cube. | 00_Laser_Clamp_OnOffSwitch | 1 | 1 | https://github.com/bionanoimaging/UC2-GIT/blob/master/CAD/ASSEMBLY_CUBE_Laser_v2/STL/00_Laser_Clamp_OnOffSwitch.stl | 0
 |  | Blue laser pointer, 445 nm | 0 | 1 | https://www.laserlands.net/11040037.html | 14.8
 |  | Screws M3x18 | 0 | 4 | https://eshop.wuerth.de/Zylinderschraube-mit-Innensechskant-SHR-ZYL-ISO4762-88-IS25-A2K-M3X18/00843%20%2018.sku/de/DE/EUR/ | 0.2
11 | ASSEMBLY_CUBE_Lens_cylindrical |  |  |  |  | 62.4 | 0 | 1 | 1 | 0 | 0 | 0 | 0 | 1 | 0 | 0 | 0 | 0 | 0 | 0 | 0
 | https://github.com/bionanoimaging/UC2-GIT/tree/master/CAD/ASSEMBLY_CUBE_Lens_CYLINDRICAL_v2 | ASSEMBLY_CUBE_empty_1x1 |  | 1 | A14;E18 | 2.2
 | 62.40 € | 20_Cube_Insert_Lens_Cylindrical | 1 | 1 | https://github.com/bionanoimaging/UC2-GIT/blob/master/CAD/ASSEMBLY_CUBE_Lens_CYLINDRICAL_v2/STL/20_Cube_Insert_Lens_Cylindrical.stl | 0.2
 | The cylindrical lens focuses a parallel beam of light into a thin line. | Cylindrical lens, f' = 63 mm (63 YQ 40) | 0 | 1 | https://www.comaroptics.com/components/lenses/cylindrical-lenses/quality-planoconvex-cylindrical-lenses-visibleuv | 60
12 | ASSEMBLY_CUBE_Lens (+40) |  |  |  |  | 8.5 | 2 | 3 | 1 | 0 | 0 | 0 | 0 | 0 | 0 | 0 | 1 | 0 | 2 | 0 | 0
 | https://github.com/bionanoimaging/UC2-GIT/tree/master/CAD/ASSEMBLY_CUBE_Lens_v2 | ASSEMBLY_CUBE_empty_1x1 |  | 1 | A14;E18 | 2.2
 | 8.50 € | 20_Lens_holder | 1 | 1 | https://github.com/bionanoimaging/UC2-GIT/blob/master/CAD/ASSEMBLY_CUBE_Lens_v2/STL/1inch_Assembly_Insert_Lens_mount_fixed_20_Lens_holder.stl | 0.3
 | This module holds a single lens precisel on the optical axis of other modules. | 20_Lens_holder_clamp | 1 | 1 | https://github.com/bionanoimaging/UC2-GIT/blob/master/CAD/ASSEMBLY_CUBE_Lens_v2/STL/1inch_Assembly_Insert_Lens_mount_fixed_20_Lens_holder_clamp.stl | 0
 |  | Lens: f'=40mm, 1 inch (Art. 2120) | 0 | 1 | https://optikbaukasten.de/ | 6
13 | ASSEMBLY_CUBE_Lens (+100) |  |  |  |  | 8.5 | 1 | 2 | 1 | 0 | 0 | 0 | 0 | 0 | 0 | 0 | 0 | 0 | 1 | 0 | 0
 | https://github.com/bionanoimaging/UC2-GIT/tree/master/CAD/ASSEMBLY_CUBE_Lens_v2 | ASSEMBLY_CUBE_empty_1x1 |  | 1 | A14;E18 | 2.2
 | 8.50 € | 20_Lens_holder | 1 | 1 | https://github.com/bionanoimaging/UC2-GIT/blob/master/CAD/ASSEMBLY_CUBE_Lens_v2/STL/1inch_Assembly_Insert_Lens_mount_fixed_20_Lens_holder.stl | 0.3
 | This module holds a single lens precisel on the optical axis of other modules. | 20_Lens_holder_clamp | 1 | 1 | https://github.com/bionanoimaging/UC2-GIT/blob/master/CAD/ASSEMBLY_CUBE_Lens_v2/STL/1inch_Assembly_Insert_Lens_mount_fixed_20_Lens_holder_clamp.stl | 0
 |  | Lens: f'=100mm, 1 inch (Art. 2004) | 0 | 1 | https://optikbaukasten.de/ | 6
14 | ASSEMBLY_CUBE_Lens (-50) |  |  |  |  | 21.5 | 1 | 0 | 1 | 0 | 0 | 0 | 0 | 0 | 0 | 0 | 0 | 0 | 1 | 0 | 0
 | https://github.com/bionanoimaging/UC2-GIT/tree/master/CAD/ASSEMBLY_CUBE_Lens_v2 | ASSEMBLY_CUBE_empty_1x1 |  | 1 | A14;E18 | 2.2
 | 21.50 € | 20_Lens_holder | 1 | 1 | https://github.com/bionanoimaging/UC2-GIT/tree/master/CAD/ASSEMBLY_CUBE_Lens_v2/STL | 0.3
 | This module holds a single lens precisel on the optical axis of other modules. | 20_Lens_holder_clamp | 1 | 1 | https://github.com/bionanoimaging/UC2-GIT/tree/master/CAD/ASSEMBLY_CUBE_Lens_v2/STL | 0
 |  | Lens: f'=-50mm, 25 mm (LC1259) | 0 | 1 | https://www.thorlabs.com/thorproduct.cfm?partnumber=LC1259 | 19
15 | ASSEMBLY_CUBE_Lens (4x) |  |  |  |  | 13.5 | 0 | 0 | 1 | 0 | 0 | 0 | 0 | 0 | 0 | 0 | 0 | 0 | 0 | 0 | 1
 | https://github.com/bionanoimaging/UC2-GIT/tree/master/CAD/ASSEMBLY_CUBE_Lens_v2 | ASSEMBLY_CUBE_empty_1x1 |  | 1 | A14;E18 | 2.2
 | 13.50 € | 20_Cube_Insert_Objective_Holder | 1 | 1 | https://github.com/bionanoimaging/UC2-GIT/blob/master/CAD/ASSEMBLY_CUBE_Lens_v2/STL/20_Cube_Insert_Objective_Holder.stl | 0.3
 |  | Microscope Objective 4x | 0 | 1 | https://de.aliexpress.com/item/32947647522.html?transAbTest=ae803_3 | 11
16 | ASSEMBLY_CUBE_Lens (+50) |  |  |  |  | 23.5 | 0 | 1 | 0 | 1 | 0 | 0 | 0 | 0 | 0 | 0 | 0 | 0 | 0 | 0 | 0
 | https://github.com/bionanoimaging/UC2-GIT/tree/master/CAD/ASSEMBLY_CUBE_Lens_v2 | ASSEMBLY_CUBE_empty_1x1 |  | 1 | A14;E18 | 2.2
 | 23.50 € | 20_Lens_holder | 1 | 1 | https://github.com/bionanoimaging/UC2-GIT/blob/master/CAD/ASSEMBLY_CUBE_Lens_v2/STL/1inch_Assembly_Insert_Lens_mount_fixed_20_Lens_holder.stl | 0.3
 | This module holds a single lens precisel on the optical axis of other modules. | 20_Lens_holder_clamp | 1 | 1 | https://github.com/bionanoimaging/UC2-GIT/blob/master/CAD/ASSEMBLY_CUBE_Lens_v2/STL/1inch_Assembly_Insert_Lens_mount_fixed_20_Lens_holder_clamp.stl | 0
 |  | Lens: f'=50mm, 1 inch (LA1131) | 0 | 1 | https://www.thorlabs.com/thorproduct.cfm?partnumber=LA1131 | 21
17 | ASSEMBLY_CUBE_Mirror_45 |  |  |  |  | 2.5 | 2 | 1 | 2 | 0 | 0 | 0 | 1 | 0 | 0 | 0 | 0 | 2 | 0 | 2 | 0
 | https://github.com/bionanoimaging/UC2-GIT/tree/master/CAD/ASSEMBLY_CUBE_Mirror_45_v2 | ASSEMBLY_CUBE_empty_1x1 |  | 1 | A14;E18 | 2.2
 | 2.50 € | 20_Cube_Insert_Mirror_Holder_30x30Mirror | 1 | 1 | https://github.com/bionanoimaging/UC2-GIT/blob/master/CAD/ASSEMBLY_CUBE_Mirror_45_v2/STL/20_Cube_Insert_Mirror_Holder_30x30Mirror_v2.stl | 0.2
 | The mirror is mounted diagonally and flips the incomong light by 90°. | 30x30 mm² Mirror | 0 | 1 | https://www.rayher.com/de/spiegelmosaik-selbstklebend-14548606 | 0.1
18 | ASSEMBLY_CUBE_Mirror_Kinematic |  |  |  |  | 4.51 | 0 | 0 | 1 | 0 | 0 | 0 | 0 | 0 | 0 | 1 | 0 | 0 | 0 | 0 | 0
 | https://github.com/bionanoimaging/UC2-GIT/tree/master/CAD/ASSEMBLY_CUBE_Mirror_Kinematic_v2 | ASSEMBLY_CUBE_empty_1x1 |  | 1 | A14;E18 | 2.2
 | 4.51 € | 20_Cube_Insert_Kinematic_Mirrormount_base | 1 | 1 | https://github.com/bionanoimaging/UC2-GIT/blob/master/CAD/ASSEMBLY_CUBE_Mirror_Kinematic_v2/STL/20_Cube_Insert_Kinematic_Mirrormount_base.stl | 0.2
 | The three-point kinematic mirror mount allows for careful alignment of the outcoming beam. | Metal plate 30x40 mm², custom cut | 0 | 1 |  | 0
 |  | 30x30 mm² Mirror | 0 | 1 | https://www.amazon.de/Rayher-14548606-Spiegelmosaik-selbstklebend-SB-Btl/dp/B008KJ8438 | 0.1
 |  | Screws M3x12 | 0 | 3 | https://eshop.wuerth.de/Zylinderschraube-mit-Innensechskant-SHR-ZYL-ISO4762-88-IS25-A2K-M3X12/00843%20%2012.sku/de/DE/EUR/ | 0.2
 |  | Ballmagnets | 0 | 3 | https://www.magnetmax.de/Neodym-Kugelmagnete/Magnetkugel-Kugelmagnet-O-5-0-mm-Neodym-vernickelt-N40-haelt-400-g::158.html | 0.47
19 | ASSEMBLY_CUBE_Mirror_Kinematic_45 |  |  |  |  | 4.61 | 0 | 0 | 1 | 0 | 0 | 0 | 0 | 1 | 2 | 0 | 0 | 0 | 0 | 0 | 1
 | https://github.com/bionanoimaging/UC2-GIT/tree/master/CAD/ASSEMBLY_CUBE_Mirror_Kinematic_45_v2 | ASSEMBLY_CUBE_empty_1x1 |  | 1 | A14;E18 | 2.2
 | 4.61 € | 20_Cube_Insert_Kinematic_Mirrormount_45_base | 1 | 1 | https://github.com/bionanoimaging/UC2-GIT/blob/master/CAD/ASSEMBLY_CUBE_Mirror_Kinematic_45_v2/STL/20_Cube_Insert_Kinematic_Mirrormount_45_base.stl | 0.3
 | The three-point kinematic mirror mount allows for careful alignment of the outcoming beam. | Metal plate 30x40 mm², custom cut | 0 | 1 |  | 0
 |  | 30x30 mm² Mirror | 0 | 1 | https://www.amazon.de/Rayher-14548606-Spiegelmosaik-selbstklebend-SB-Btl/dp/B008KJ8438 | 0.1
 |  | Screws M3x12 | 0 | 3 | https://eshop.wuerth.de/Zylinderschraube-mit-Innensechskant-SHR-ZYL-ISO4762-88-IS25-A2K-M3X12/00843%20%2012.sku/de/DE/EUR/ | 0.2
 |  | Ballmagnets | 0 | 3 | https://www.magnetmax.de/Neodym-Kugelmagnete/Magnetkugel-Kugelmagnet-O-5-0-mm-Neodym-vernickelt-N40-haelt-400-g::158.html | 0.47
20 | ASSEMBLY_CUBE_RaspiCam |  |  |  |  | 33.7 | 0 | 0 | 1 | 2 | 1 | 1 | 1 | 1 | 1 | 1 | 0 | 0 | 0 | 0 | 1
 | https://github.com/bionanoimaging/UC2-GIT/tree/master/CAD/ASSEMBLY_CUBE_RaspiCam_v2 | ASSEMBLY_CUBE_empty_1x1 |  | 1 | A14;E18 | 2.2
 | 33.70 € | 20_Cube_Insert_RaspiCam | 1 | 1 | https://github.com/bionanoimaging/UC2-GIT/blob/master/CAD/ASSEMBLY_CUBE_RaspiCam_v2/STL/20_Cube_Insert_RaspiCam.stl | 0.3
 | The camera module serves for image acquisition. | Raspberry Pi Camera | 0 | 1 | https://www.amazon.de/Raspberry-Pi-v2-1-1080P-Kamera-Modul/dp/B01ER2SMHY?__mk_de_DE=%C3%85M%C3%85%C5%BD%C3%95%C3%91&s=gateway | 27
 |  | Raspberry Pi Camera long cable | 0 | 1 | https://www.amazon.de/gp/product/B075JN61S7/ref=ox_sc_act_title_2?smid=A1X7QLRQH87QA3&psc=1 | 4
 |  | M2 screw + nut | 0 | 2 | https://www.amazon.de/Edelstahl-Sechskopf-Knopf-Schrauben-Unterlegscheiben-Sortiment-Aufbewahrung/dp/B073SS7D8J?__mk_de_DE=%C3%85M%C3%85%C5%BD%C3%95%C3%91&s=diy | 0.1
21 | ASSEMBLY_CUBE_S-Stage |  |  |  |  | 21.75 | 0 | 0 | 1 | 0 | 0 | 0 | 0 | 1 | 0 | 0 | 0 | 0 | 0 | 0 | 0
 | https://github.com/bionanoimaging/UC2-GIT/tree/master/CAD/ASSEMBLY_CUBE_S-STAGE_v2 | 10_Lid_1x1_v2_thin | 1 | 1 | https://github.com/bionanoimaging/UC2-GIT/blob/master/CAD/ASSEMBLY_CUBE_S-STAGE_v2/STL/10_Lid_1x1_v2_thin.stl | 0.2
 | 21.75 € | 30_Z_Translator_Lightsheet | 1 | 1 | https://github.com/bionanoimaging/UC2-GIT/blob/master/CAD/ASSEMBLY_CUBE_S-STAGE_v2/STL/30_Z_Translator_Lightsheet_v4.stl | 0.5
 | The sample stage allows for precise movement of the sample along one axis. | 30_Coupling_Screw_28BYJ_M3 | 1 | 1 | https://github.com/bionanoimaging/UC2-GIT/blob/master/CAD/ASSEMBLY_CUBE_S-STAGE_v2/STL/30_Coupling_Screw_28BYJ_M3.stl | 0
 |  | Screws M3x12 | 0 | 6 | https://eshop.wuerth.de/Zylinderschraube-mit-Innensechskant-SHR-ZYL-ISO4762-88-IS25-A2K-M3X12/00843%20%2012.sku/de/DE/EUR/ | 0.2
 |  | M3x25 screw with nut (non-magnetic) | 0 | 1 | https://www.amazon.de/Edelstahl-Sechskopf-Knopf-Schrauben-Unterlegscheiben-Sortiment-Aufbewahrung/dp/B073SS7D8J?__mk_de_DE=%C3%85M%C3%85%C5%BD%C3%95%C3%91&s=diy | 0.1
 |  | Metal plate 30x40 mm², custom cut | 0 | 1 |  | 0
 |  | 30_Syringe_holder | 1 | 1 | https://github.com/bionanoimaging/UC2-GIT/blob/master/CAD/ASSEMBLY_CUBE_S-STAGE_v2/STL/30_Syringe_holder_v2.stl | 0
 |  | ESP32 | 0 | 1 | https://www.amazon.de/AZDelivery-NodeMCU-Development-Nachfolgermodell-ESP8266/dp/B074RGW2VQ?__mk_de_DE=%C3%85M%C3%85%C5%BD%C3%95%C3%91&s=gateway | 8
 |  | 28-BYJ stepper motor with driver board | 0 | 1 | https://www.reichelt.de/entwicklerboards-schrittmotor-inkl-steuerung-uln2003-debo-moto1-p192146.html | 5.35
 |  | Female-Female Jumper Wire | 0 | 6 | https://www.amazon.de/-/en/AZDelivery-Jumper-Arduino-Raspberry-Breadboard/dp/B07KYHBVR7 | 0.6
 |  | USB-microUSB cable | 0 | 1 | https://www.amazon.de/dp/B0778FV6K4?fst=as%3Aoff&rnid=669059031&s=computers | 2.8
22 | ASSEMBLY_CUBE_Sample_Holder |  |  |  |  | 2.5 | 0 | 5 | 1 | 1 | 1 | 0 | 0 | 0 | 2 | 1 | 1 | 0 | 0 | 0 | 2
 | https://github.com/bionanoimaging/UC2-GIT/tree/master/CAD/ASSEMBLY_CUBE_Sample_Holder_v2 | ASSEMBLY_CUBE_empty_1x1 |  | 1 | A14;E18 | 2.2
 | 2.50 € | 20_Cube_insert_Sample_holder | 1 | 1 | https://github.com/bionanoimaging/UC2-GIT/blob/master/CAD/ASSEMBLY_CUBE_Sample_Holder_v2/STL/20_Cube_insert_Sample_holder.stl | 0.3
 | The sample holder is optimal for microscope slides or other thin objects. | 20_Cube_Insert_Sample_clamp | 1 | 1 | https://github.com/bionanoimaging/UC2-GIT/blob/master/CAD/ASSEMBLY_CUBE_Sample_Holder_v2/STL/20_Cube_Insert_Sample_clamp.stl | 0
23 | ASSEMBLY_CUBE_Sample_Comb |  |  |  |  | 1.4 | 0 | 0 | 1 | 0 | 0 | 0 | 0 | 0 | 0 | 0 | 0 | 0 | 0 | 0 | 0
 | https://github.com/bionanoimaging/UC2-GIT/tree/master/CAD/ASSEMBLY_CUBE_Sample_Holder_v2 | 10_Lid_1x1 | 1 | 1 | https://github.com/bionanoimaging/UC2-GIT/blob/master/CAD/ASSEMBLY_CUBE_Base_v2/STL/10_Lid_1x1_v2.stl | 0.2
 | 1.40 € | 20_Cube_Sampleholder | 1 | 1 | https://github.com/bionanoimaging/UC2-GIT/blob/master/CAD/ASSEMBLY_CUBE_Sample_Holder_v2/STL/20_Cube_Sampleholder.stl | 0.4
 | The comb shaped sample holder can hold object of various sizes. | Screws M3x12 | 0 | 4 | https://eshop.wuerth.de/Zylinderschraube-mit-Innensechskant-SHR-ZYL-ISO4762-88-IS25-A2K-M3X12/00843%20%2012.sku/de/DE/EUR/ | 0.2
24 | ASSEMBLY_CUBE_Z-stage |  |  |  |  | 50.35 | 0 | 0 | 1 | 0 | 0 | 0 | 1 | 1 | 0 | 0 | 0 | 0 | 0 | 1 | 0
 | https://github.com/bionanoimaging/UC2-GIT/tree/master/CAD/ASSEMBLY_CUBE_Z-STAGE_v2 | 10_Cube_2x1 | 1 | 1 | https://github.com/bionanoimaging/UC2-GIT/blob/master/CAD/ASSEMBLY_CUBE_Z-STAGE_v2/STL/10_Cube_2x1_v2.stl | 0.5
 | 50.35 € | 10_Lid_el_2x1 | 1 | 1 | https://github.com/bionanoimaging/UC2-GIT/blob/master/CAD/ASSEMBLY_CUBE_Z-STAGE_v2/STL/10_Lid_el_2x1_v2.stl | 0.3
 | The linearflexure mechanism of the Z-stage is used for precise focussing of the microscope objective. Motors used. | 20_focus_inlet_linearflexure | 1 | 1 | https://github.com/bionanoimaging/UC2-GIT/blob/master/CAD/ASSEMBLY_CUBE_Z-STAGE_v2/STL/20_focus_inlet_linearflexure_v0.stl | 0.6
 |  | 30_Coupling_Screw_28BYJ_M3 | 1 | 1 | https://github.com/bionanoimaging/UC2-GIT/blob/master/CAD/ASSEMBLY_CUBE_Z-STAGE_v2/STL/30_Coupling_Screw_28BYJ_M3.stl | 0
 |  | 30_focus_inlet_objective_mount | 1 | 1 | https://github.com/bionanoimaging/UC2-GIT/blob/master/CAD/ASSEMBLY_CUBE_Z-STAGE_v2/STL/30_focus_inlet_objective_mount_v7.stl | 0.1
 |  | 30_Z_Stage_Adapterplate | 1 | 1 | https://github.com/bionanoimaging/UC2-GIT/blob/master/CAD/ASSEMBLY_CUBE_Z-STAGE_v2/STL/30_Z_Stage_Adapterplate.stl | 0.3
 |  | 30_Z_Stage_Fluomodule | 1 | 1 | https://github.com/bionanoimaging/UC2-GIT/blob/master/CAD/ASSEMBLY_CUBE_Z-STAGE_v2/STL/30_Z_Stage_Fluomodule.stl | 0.2
 |  | 40_XY_Stage_Clamp_Slide | 1 | 1 | https://github.com/bionanoimaging/UC2-GIT/blob/master/CAD/ASSEMBLY_CUBE_Z-STAGE_v2/STL/40_XY_Stage_Clamp_Slide.stl | 0.1
 |  | Microscope Objective 10x | 0 | 1 | https://de.aliexpress.com/item/32947647522.html?transAbTest=ae803_3 | 15.4
 |  | Screws M3x12 | 0 | 20 | https://eshop.wuerth.de/Zylinderschraube-mit-Innensechskant-SHR-ZYL-ISO4762-88-IS25-A2K-M3X12/00843%20%2012.sku/de/DE/EUR/ | 0.6
 |  | Screws M3x8 | 0 | 3 | https://eshop.wuerth.de/Zylinderschraube-mit-Innensechskant-SHR-ZYL-ISO4762-88-IS25-A2K-M3X8/00843%20%208.sku/de/DE/EUR/ | 0.2
 |  | M3x30 screw with nut (non-magnetic) | 0 | 1 | https://www.amazon.de/Edelstahl-Sechskopf-Knopf-Schrauben-Unterlegscheiben-Sortiment-Aufbewahrung/dp/B073SS7D8J?__mk_de_DE=%C3%85M%C3%85%C5%BD%C3%95%C3%91&s=diy | 0.1
 |  | Screws M3x18 | 0 | 2 | https://eshop.wuerth.de/Zylinderschraube-mit-Innensechskant-SHR-ZYL-ISO4762-88-IS25-A2K-M3X18/00843%20%2018.sku/de/DE/EUR/ | 0.2
 |  | ESP32 | 0 | 1 | https://www.amazon.de/AZDelivery-NodeMCU-Development-Nachfolgermodell-ESP8266/dp/B074RGW2VQ?__mk_de_DE=%C3%85M%C3%85%C5%BD%C3%95%C3%91&s=gateway | 8
 |  | 28-BYJ stepper motor with driver board | 0 | 1 | https://www.reichelt.de/entwicklerboards-schrittmotor-inkl-steuerung-uln2003-debo-moto1-p192146.html | 5.35
 |  | Female-Female Jumper Wire | 0 | 6 | https://www.amazon.de/-/en/AZDelivery-Jumper-Arduino-Raspberry-Breadboard/dp/B07KYHBVR7 | 0.6
 |  | USB-microUSB cable | 0 | 1 | https://www.amazon.de/dp/B0778FV6K4?fst=as%3Aoff&rnid=669059031&s=computers | 2.8
25 | ASSEMBLY_CUBE_Z-stage_mechanical |  |  |  |  | 30.7 | 1 | 1 | 0 | 0 | 0 | 0 | 0 | 0 | 0 | 0 | 0 | 1 | 0 | 0 | 0
 | https://github.com/bionanoimaging/UC2-GIT/tree/master/CAD/ASSEMBLY_CUBE_Z-STAGE_mechanical_v2 | 10_Cube_2x1 | 1 | 1 | https://github.com/bionanoimaging/UC2-GIT/blob/master/CAD/ASSEMBLY_CUBE_Z-STAGE_mechanical_v2/STL/Assembly_Z-Focus_Linearbearing_mechanical_v0_10_Cube_2x1_v2.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 | 0.5
 | 30.70 € | 10_Lid_el_2x1 | 1 | 1 | https://github.com/bionanoimaging/UC2-GIT/blob/master/CAD/ASSEMBLY_CUBE_Z-STAGE_mechanical_v2/STL/Assembly_Z-Focus_Linearbearing_mechanical_v0_10_Lid_el_2x1_v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 | 0.3
 | The linearflexure mechanism of the Z-stage is used for precise focussing of the microscope objective. Mechanical only. | 20_focus_inlet_linearflexure | 1 | 1 | https://github.com/bionanoimaging/UC2-GIT/blob/master/CAD/ASSEMBLY_CUBE_Z-STAGE_mechanical_v2/STL/Assembly_Z-Focus_Linearbearing_mechanical_v0_20_focus_inlet_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 | 0.6
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

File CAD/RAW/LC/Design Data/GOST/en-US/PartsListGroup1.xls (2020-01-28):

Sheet: Лист 1
Инв. № подл |  |  |  | Подп. и дата | Взам. инв. № | Инв. № дубл. |  |  | Подп. и дата
Формат | Зона | Поз. | Обозначение |  |  |  | Наименование |  |  |  |  |  | Кол. на исполнение
 |  |  |  |  |  |  |  |  |  |  |  | Лит.
 |  |  |  |  |  |  |  |  |  |  |  | Код
 |  |  |  |  |  |  |  | Изм. | Лист | № докум | Подпись |  | Дата
 |  |  |  |  |  |  |  | Разраб.
 |  |  |  |  |  |  |  | Пров.
 |  |  |  |  |  |  |  | Н.контр
 |  |  |  |  |  |  |  | Утв.
 |  |  |  |  |  |  |  |  |  |  |  |  |  | Копировал

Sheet: Лист 2
Инв. № подл |  |  |  | Подп. и дата | Взам. инв. № | Инв. № дубл. |  |  | Подп. и дата
Формат | Зона | Поз. | Обозначение |  |  |  | Наименование |  |  |  |  | Кол. на исполнение
 |  |  |  |  |  |  |  | Изм. | Лист | № докум. | Подп. | Дата
 |  |  |  |  |  |  |  |  |  |  |  |  | Копировал
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

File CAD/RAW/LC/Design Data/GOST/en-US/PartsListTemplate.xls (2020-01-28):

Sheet: Лист 1
 | Формат | Зона |  | Поз. |  | Обозначение |  |  |  | Наименование |  |  |  | Кол. | Приме-чание
Подп. и дата
Инв. № дубл.
Взам. инв. №
Подп. и дата
 | Изм. |  | Лист |  | № докум |  | Подпись | Дата
Инв. № подл | Разраб. |  |  |  |  |  |  |  |  |  | Литера |  | Лист |  |  | Листов
 | Пров.
 | Н.контр
 | Утв.
 |  |  |  |  |  |  |  |  | Копировал |  |  | Формат А4

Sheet: Лист 2
 | Формат | Зона |  | Поз. |  | Обозначение |  |  |  | Наименование |  | Кол. | Приме-чание
Подп. и дата
Инв. № дубл.
Взам. инв. №
Подп. и дата
Инв. № подл
 | Изм. |  | Лист |  | № докум. |  | Подп. |  | Дата
 |  |  |  |  |  |  |  | Копировал |  |  | Формат А4
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

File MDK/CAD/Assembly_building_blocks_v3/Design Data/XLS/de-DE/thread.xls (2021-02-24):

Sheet: Inch Tapping Threads
I Q X | Zoll-Blechschraubgewinde |  | Sort Order - 5 |  | External |  |  |  |  |  |  | Internal
 |  |  |  |  |  | Major Dia |  | Pitch Dia |  | Minor Dia |  |  | Minor Dia |  | Pitch Dia |  | Major Dia |  | Tap Drill
Size | Size Suffix | Thread Designation | Custom Thread Designation | TPI | Class | Max | Min | Max | Min | Max | Min | Class | Min | Max | Min | Max | Min | Max | Basic
0.0600 |  | 0-48 | 0-48 | 48 | 2B | 0.0600 | 0.0540 | 0.0480 | 0.0435 | 0.0360 | 0.0330
0.0730 |  | 1-42 | 1-42 | 42 | 2B | 0.0750 | 0.0690 | 0.0620 | 0.0575 | 0.0490 | 0.0460
0.0860 |  | 2-32 | 2-32 | 32 | 2B | 0.0880 | 0.0820 | 0.0760 | 0.0710 | 0.0640 | 0.0600
0.0990 |  | 3-28 | 3-28 | 28 | 2B | 0.1010 | 0.0950 | 0.0880 | 0.0830 | 0.0750 | 0.0710
0.1120 |  | 4-24 | 4-24 | 24 | 2B | 0.1140 | 0.1080 | 0.1000 | 0.0950 | 0.0860 | 0.0820
0.1250 |  | 5-20 | 5-20 | 20 | 2B | 0.1300 | 0.1230 | 0.1120 | 0.1065 | 0.0940 | 0.0900
0.1380 |  | 6-20 | 6-20 | 20 | 2B | 0.1390 | 0.1320 | 0.1215 | 0.1155 | 0.1040 | 0.0990
0.1510 |  | 7-19 | 7-19 | 19 | 2B | 0.1540 | 0.1470 | 0.1345 | 0.1280 | 0.1150 | 0.1090
0.1640 |  | 8-18 | 8-18 | 18 | 2B | 0.1660 | 0.1590 | 0.1440 | 0.1375 | 0.1220 | 0.1160
0.1900 |  | 10-16 | 10-16 | 16 | 2B | 0.1890 | 0.1820 | 0.1650 | 0.1585 | 0.1410 | 0.1350
0.2160 |  | 12-14 | 12-14 | 14 | 2B | 0.2150 | 0.2080 | 0.1895 | 0.1825 | 0.1640 | 0.1570
0.2420 |  | 14-14 | 14-14 | 14 | 2B | 0.2410 | 0.2340 | 0.2130 | 0.2060 | 0.1850 | 0.1780
0.2500 |  | 1/4-14 | 1/4-14 | 14 | 2B | 0.2460 | 0.2370 | 0.2190 | 0.2110 | 0.1920 | 0.1850
0.3125 |  | 5/16-12 | 5/16-12 | 12 | 2B | 0.3150 | 0.3060 | 0.2795 | 0.2710 | 0.2440 | 0.2360
0.3750 |  | 3/8-12 | 3/8-12 | 12 | 2B | 0.3800 | 0.3710 | 0.3445 | 0.3350 | 0.3090 | 0.2990
0.4375 |  | 7/16-10 | 7/16-10 | 10 | 2B | 0.4400 | 0.4290 | 0.3995 | 0.3890 | 0.3590 | 0.3490
0.5000 |  | 1/2-10 | 1/2-10 | 10 | 2B | 0.5040 | 0.4930 | 0.4635 | 0.4530 | 0.4230 | 0.4130

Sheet: Metric Forming Screw Threads
M P X | Metrisch geform. Schraubgewinde |  | Sort Order - 6 |  | External |  |  |  |  |  |  | Internal
 |  |  |  |  |  | Major Dia |  | Pitch Dia |  | Minor Dia |  |  | Minor Dia |  | Pitch Dia |  | Major Dia |  | Tap Drill
Size | Size Suffix | Thread Designation | Custom Thread Designation | Pitch | Class | Max | Min | Max | Min | Max | Min | Class | Min | Max | Min | Max | Min | Max | Basic
1.5 |  | 1.5x0.5 | 1.5x0.5 | 0.5 | 6g | 1.520 | 1.380 | 1.215 | 1.110 | 0.910 | 0.840
1.5 |  | ST1.5x0.5 | ST1.5x0.5 | 0.5 | 6g | 1.520 | 1.380 | 1.215 | 1.110 | 0.910 | 0.840
1.9 |  | 1.9x0.6 | 1.9x0.6 | 0.6 | 6g | 1.900 | 1.760 | 1.570 | 1.465 | 1.240 | 1.170
1.9 |  | ST1.9x0.6 | ST1.9x0.6 | 0.6 | 6g | 1.900 | 1.760 | 1.570 | 1.465 | 1.240 | 1.170
2.2 |  | 2.2x0.8 | 2.2x0.8 | 0.8 | 6g | 2.240 | 2.100 | 1.935 | 1.810 | 1.630 | 1.520
2.2 |  | ST2.2x0.8 | ST2.2x0.8 | 0.8 | 6g | 2.240 | 2.100 | 1.935 | 1.810 | 1.630 | 1.520
2.6 |  | 2.6x0.9 | 2.6x0.9 | 0.9 | 6g | 2.570 | 2.430 | 2.235 | 2.115 | 1.900 | 1.800
2.6 |  | ST2.6x0.9 | ST2.6x0.9 | 0.9 | 6g | 2.570 | 2.430 | 2.235 | 2.115 | 1.900 | 1.800
2.9 |  | 2.9x1 | 2.9x1 | 1 | 6g | 2.900 | 2.760 | 2.540 | 2.420 | 2.180 | 2.080
2.9 |  | 2.9x1.1 | 2.9x1.1 | 1.1 | 6g | 2.900 | 2.760 | 2.540 | 2.420 | 2.180 | 2.080
2.9 |  | ST2.9x1.1 | ST2.9x1.1 | 1.1 | 6g | 2.900 | 2.760 | 2.540 | 2.420 | 2.180 | 2.080
2.9 |  | 2.9x1.3 | 2.9x1.3 | 1.3 | 6g | 2.900 | 2.720 | 2.540 | 2.355 | 1.890 | 1.700
2.9 |  | 2.9x1.4 | 2.9x1.4 | 1.4 | 6g | 2.900 | 2.720 | 2.340 | 2.175 | 1.780 | 1.630
3.3 |  | 3.3x1.3 | 3.3x1.3 | 1.3 | 6g | 3.300 | 3.120 | 2.795 | 2.665 | 2.290 | 2.210
3.3 |  | ST3.3x1.3 | ST3.3x1.3 | 1.3 | 6g | 3.300 | 3.120 | 2.795 | 2.665 | 2.290 | 2.210
3.5 |  | 3.5x1.3 | 3.5x1.3 | 1.3 | 6g | 3.530 | 3.350 | 3.085 | 2.930 | 2.640 | 2.510
3.5 |  | ST3.5x1.3 | ST3.5x1.3 | 1.3 | 6g | 3.530 | 3.350 | 3.085 | 2.930 | 2.640 | 2.510
3.5 |  | 3.5x1.6 | 3.5x1.6 | 1.6 | 6g | 3.530 | 3.350 | 2.920 | 2.755 | 2.310 | 2.160
3.5 |  | 3.5x3.2 | 3.5x3.2 | 3.2 | 6g | 3.530 | 3.310 | 2.800 | 2.600 | 2.070 | 1.890
3.9 |  | 3.9x1.3 | 3.9x1.3 | 1.3 | 6g | 3.910 | 3.730 | 3.415 | 3.250 | 2.920 | 2.770
3.9 |  | ST3.9x1.3 | ST3.9x1.3 | 1.3 | 6g | 3.910 | 3.730 | 3.415 | 3.250 | 2.920 | 2.770
3.9 |  | 3.9x1.6 | 3.9x1.6 | 1.6 | 6g | 3.910 | 3.730 | 3.300 | 3.135 | 2.690 | 2.540
3.9 |  | 3.9x3.2 | 3.9x3.2 | 3.2 | 6g | 3.910 | 3.690 | 3.180 | 2.980 | 2.450 | 2.270
4.2 |  | 4.2x1.4 | 4.2x1.4 | 1.4 | 6g | 4.220 | 4.040 | 3.660 | 3.495 | 3.100 | 2.950
4.2 |  | ST4.2x1.4 | ST4.2x1.4 | 1.4 | 6g | 4.220 | 4.040 | 3.660 | 3.495 | 3.100 | 2.950
4.2 |  | 4.2x1.6 | 4.2x1.6 | 1.6 | 6g | 4.220 | 4.040 | 3.610 | 3.445 | 3.000 | 2.850
4.2 |  | 4.2x3.2 | 4.2x3.2 | 3.2 | 6g | 4.220 | 4.000 | 3.380 | 3.180 | 2.540 | 2.360
4.8 |  | 4.8x1.6 | 4.8x1.6 | 1.6 | 6g | 4.800 | 4.620 | 4.190 | 4.025 | 3.580 | 3.430
4.8 |  | ST4.8x1.6 | ST4.8x1.6 | 1.6 | 6g | 4.800 | 4.620 | 4.190 | 4.025 | 3.580 | 3.430
4.8 |  | 4.8x1.8 | 4.8x1.8 | 1.8 | 6g | 4.800 | 4.620 | 4.065 | 3.885 | 3.330 | 3.150
4.8 |  | 4.8x3.2 | 4.8x3.2 | 3.2 | 6g | 4.800 | 4.580 | 3.960 | 3.760 | 3.120 | 2.940
5.5 |  | 5.5x1.8 | 5.5x1.8 | 1.8 | 6g | 5.460 | 5.280 | 4.815 | 4.635 | 4.170 | 3.990
5.5 |  | ST5.5x1.8 | ST5.5x1.8 | 1.8 | 6g | 5.460 | 5.280 | 4.815 | 4.635 | 4.170 | 3.990
6.3 |  | 6.3x1.8 | 6.3x1.8 | 1.8 | 6g | 6.250 | 6.030 | 5.565 | 5.365 | 4.880 | 4.700
6.3 |  | ST6.3x1.8 | ST6.3x1.8 | 1.8 | 6g | 6.250 | 6.030 | 5.565 | 5.365 | 4.880 | 4.700
8.0 |  | 8x2.1 | 8x2.1 | 2.1 | 6g | 8.000 | 7.780 | 7.100 | 6.885 | 6.200 | 5.990
8.0 |  | ST8x2.1 | ST8x2.1 | 2.1 | 6g | 8.000 | 7.780 | 7.100 | 6.885 | 6.200 | 5.990
9.5 |  | 9.5x2.1 | 9.5x2.1 | 2.1 | 6g | 9.650 | 9.430 | 8.750 | 8.510 | 7.850 | 7.590
9.5 |  | ST9.5x2.1 | ST9.5x2.1 | 2.1 | 6g | 9.650 | 9.430 | 8.750 | 8.510 | 7.850 | 7.590

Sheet: ISO Pipe Threads
M Q | ISO-Rohrgewinde |  | Sort Order - 9 |  | External |  |  |  |  |  |  | Internal
 |  |  |  |  |  | Major Dia |  | Pitch Dia |  | Minor Dia |  |  | Minor Dia |  | Pitch Dia |  | Major Dia |  | Tap Drill | Thread Depth | Thread Runouts
Size | Size Suffix | Thread Designation | Custom Thread Designation | TPI | Class | Max | Min | Max | Min | Max | Min | Class | Min | Max | Min | Max | Min | Max | Basic
7.723 |  | G7.723x0.907 | G 1/16 | 28 | A | 7.723 | 7.509 | 7.142 | 7.035 | 6.561 |  |  | 6.561 | 6.834 | 7.142 | 7.249 | 7.723 |  | 1.5875 | 15.446 | 4.5000
7.723 |  | G7.723x0.907 | G 1/16 | 28 | B | 7.723 | 7.509 | 7.142 | 6.928 | 6.561
9.728 |  | G9.728x0.907 | G 1/8 | 28 | A | 9.728 | 9.514 | 9.147 | 9.040 | 8.566 |  |  | 8.566 | 8.848 | 9.147 | 9.254 | 9.728 |  | 3.1750 | 19.456 | 4.5000
9.728 |  | G9.728x0.907 | G 1/8 | 28 | B | 9.728 | 9.514 | 9.147 | 8.933 | 8.566
13.157 |  | G13.157x1.337 | G 1/4 | 19 | A | 13.157 | 12.907 | 12.301 | 12.176 | 11.445 |  |  | 11.445 | 11.89 | 12.301 | 12.426 | 13.157 |  | 6.3500 | 26.314 | 6.5000
13.157 |  | G13.157x1.337 | G 1/4 | 19 | B | 13.157 | 12.907 | 12.301 | 12.051 | 11.445
16.662 |  | G16.662x1.337 | G 3/8 | 19 | A | 16.662 | 16.412 | 15.806 | 15.681 | 14.950 |  |  | 14.95 | 15.395 | 15.806 | 15.931 | 16.662 |  | 9.5250 | 33.324 | 6.5000
16.662 |  | G16.662x1.337 | G 3/8 | 19 | B | 16.662 | 16.412 | 15.806 | 15.556 | 14.950
20.955 |  | G20.955x1.814 | G 1/2 | 14 | A | 20.955 | 20.671 | 19.793 | 19.651 | 18.631 |  |  | 18.631 | 19.172 | 19.793 | 19.935 | 20.955 |  | 12.7000 | 41.910 | 8.5000
20.955 |  | G20.955x1.814 | G 1/2 | 14 | B | 20.955 | 20.671 | 19.793 | 19.509 | 18.631
22.911 |  | G22.911x1.814 | G 5/8 | 14 | A | 22.911 | 22.627 | 21.749 | 21.607 | 20.587 |  |  | 20.587 | 21.128 | 21.749 | 21.891 | 22.911 |  |  | 45.822 | 8.5000
22.911 |  | G22.911x1.814 | G 5/8 | 14 | B | 22.911 | 22.627 | 21.749 | 21.465 | 20.587
26.441 |  | G26.441x1.814 | G 3/4 | 14 | A | 26.441 | 26.157 | 25.279 | 25.137 | 24.117 |  |  | 24.117 | 24.658 | 25.279 | 25.421 | 26.441 |  | 15.8750 | 52.882 | 8.5000
26.441 |  | G26.441x1.814 | G 3/4 | 14 | B | 26.441 | 26.157 | 25.279 | 24.995 | 24.117
30.201 |  | G30.201x1.814 | G 7/8 | 14 | A | 30.201 | 29.917 | 29.039 | 28.897 | 27.877 |  |  | 27.877 | 28.418 | 29.039 | 29.181 | 30.201 |  | 22.2250 | 60.402 | 8.5000
30.201 |  | G30.201x1.814 | G 7/8 | 14 | B | 30.201 | 29.917 | 29.039 | 28.755 | 27.877
33.249 |  | G33.249x2.309 | G 1 | 11 | A | 33.249 | 32.889 | 31.770 | 31.590 | 30.291 |  |  | 30.291 | 30.931 | 31.77 | 31.95 | 33.249 |  | 25.4000 | 66.498 | 10.0000
33.249 |  | G33.249x2.309 | G 1 | 11 | B | 33.249 | 32.889 | 31.770 | 31.410 | 30.291
37.897 |  | G37.897x2.309 | G 1 1/8 | 11 | A | 37.897 | 37.537 | 36.418 | 36.238 | 34.939 |  |  | 34.939 | 35.579 | 36.418 | 36.598 | 37.897 |  | 28.5750 | 75.794 | 10.0000
37.897 |  | G37.897x2.309 | G 1 1/8 | 11 | B | 37.897 | 37.537 | 36.418 | 36.058 | 34.939
41.910 |  | G41.91x2.309 | G 1 1/4 | 11 | A | 41.910 | 41.550 | 40.431 | 40.251 | 38.952 |  |  | 38.952 | 39.592 | 40.431 | 40.611 | 41.910 |  | 31.7500 | 83.820 | 10.0000
41.910 |  | G41.91x2.309 | G 1 1/4 | 11 | B | 41.910 | 41.550 | 40.431 | 40.071 | 38.952
47.803 |  | G47.803x2.309 | G 1 1/2 | 11 | A | 47.803 | 47.443 | 46.324 | 46.144 | 44.845 |  |  | 44.845 | 45.485 | 46.324 | 46.504 | 47.803 |  | 38.1000 | 95.606 | 10.0000
47.803 |  | G47.803x2.309 | G 1 1/2 | 11 | B | 47.803 | 47.443 | 46.324 | 45.964 | 44.845
53.746 |  | G53.746x2.309 | G 1 3/4 | 11 | A | 53.746 | 53.386 | 52.267 | 52.087 | 50.788 |  |  | 50.788 | 51.428 | 52.267 | 52.447 | 53.746 |  | 44.4500 | 107.492 | 10.0000
53.746 |  | G53.746x2.309 | G 1 3/4 | 11 | B | 53.746 | 53.386 | 52.267 | 51.907 | 50.788
59.614 |  | G59.614x2.309 | G 2 | 11 | A | 59.614 | 59.254 | 58.135 | 57.955 | 56.656 |  |  | 56.656 | 57.296 | 58.135 | 58.315 | 59.614 |  | 50.8000 | 119.228 | 10.0000
59.614 |  | G59.614x2.309 | G 2 | 11 | B | 59.614 | 59.254 | 58.135 | 57.775 | 56.656
65.710 |  | G65.71x2.309 | G 2 1/4 | 11 | A | 65.710 | 65.276 | 64.231 | 64.014 | 62.752 |  |  | 62.752 | 63.392 | 64.231 | 64.448 | 65.710 |  | 57.1500 | 131.420 | 10.0000
65.710 |  | G65.71x2.309 | G 2 1/4 | 11 | B | 65.710 | 65.276 | 64.231 | 63.797 | 62.752
75.184 |  | G75.184x2.309 | G 2 1/2 | 11 | A | 75.184 | 74.750 | 73.705 | 73.488 | 72.226 |  |  | 72.226 | 72.866 | 73.705 | 73.922 | 75.184 |  |  | 150.368 | 10.0000
75.184 |  | G75.184x2.309 | G 2 1/2 | 11 | B | 75.184 | 74.750 | 73.705 | 73.271 | 72.226
81.534 |  | G81.534x2.309 | G 2 3/4 | 11 | A | 81.534 | 81.100 | 80.055 | 79.838 | 78.576 |  |  | 78.576 | 79.216 | 80.055 | 80.272 | 81.534 |  | 69.8500 | 163.068 | 10.0000
81.534 |  | G81.534x2.309 | G 2 3/4 | 11 | B | 81.534 | 81.100 | 80.055 | 79.621 | 78.576
87.884 |  | G87.884x2.309 | G 3 | 11 | A | 87.884 | 87.450 | 86.405 | 86.188 | 84.926 |  |  | 84.926 | 85.566 | 86.405 | 86.622 | 87.884 |  | 76.2000 | 175.768 | 10.0000
87.884 |  | G87.884x2.309 | G 3 | 11 | B | 87.884 | 87.450 | 86.405 | 85.971 | 84.926
100.330 |  | G100.33x2.309 | G 3 1/2 | 11 | A | 100.330 | 99.896 | 98.851 | 98.634 | 97.372 |  |  | 97.372 | 98.012 | 98.851 | 99.068 | 100.330 |  | 88.9000 | 200.660 | 10.0000
100.330 |  | G100.33x2.309 | G 3 1/2 | 11 | B | 100.330 | 99.896 | 98.851 | 98.417 | 97.372
113.030 |  | G113.03x2.309 | G 4 | 11 | A | 113.030 | 112.596 | 111.551 | 111.334 | 110.072 |  |  | 110.072 | 110.712 | 111.551 | 111.768 | 113.030 |  | 101.6000 | 226.060 | 10.0000
113.030 |  | G113.03x2.309 | G 4 | 11 | B | 113.030 | 112.596 | 111.551 | 111.117 | 110.072
125.730 |  | G125.73x2.309 | G 4 1/2 | 11 | A | 125.730 | 125.296 | 124.251 | 124.034 | 122.772 |  |  | 122.772 | 123.412 | 124.251 | 124.468 | 125.730 |  | 114.3000 | 251.460 | 10.0000
125.730 |  | G125.73x2.309 | G 4 1/2 | 11 | B | 125.730 | 125.296 | 124.251 | 123.817 | 122.772
138.430 |  | G138.43x2.309 | G 5 | 11 | A | 138.430 | 137.996 | 136.951 | 136.734 | 135.472 |  |  | 135.472 | 136.112 | 136.951 | 137.168 | 138.430 |  | 127.0000 | 276.860 | 10.0000
138.430 |  | G138.43x2.309 | G 5 | 11 | B | 138.430 | 137.996 | 136.951 | 136.517 | 135.472
151.130 |  | G151.13x2.309 | G 5 1/2 | 11 | A | 151.130 | 150.696 | 149.651 | 149.434 | 148.172 |  |  | 148.172 | 148.812 | 149.651 | 149.868 | 151.130 |  | 139.7000 | 302.260 | 10.0000
151.130 |  | G151.13x2.309 | G 5 1/2 | 11 | B | 151.130 | 150.696 | 149.651 | 149.217 | 148.172
163.830 |  | G163.83x2.309 | G 6 | 11 | A | 163.830 | 163.396 | 162.351 | 162.134 | 160.872 |  |  | 160.872 | 161.512 | 162.351 | 162.568 | 163.830 |  | 152.4000 | 327.660 | 10.0000
163.830 |  | G163.83x2.309 | G 6 | 11 | B | 163.830 | 163.396 | 162.351 | 161.917 | 160.872
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

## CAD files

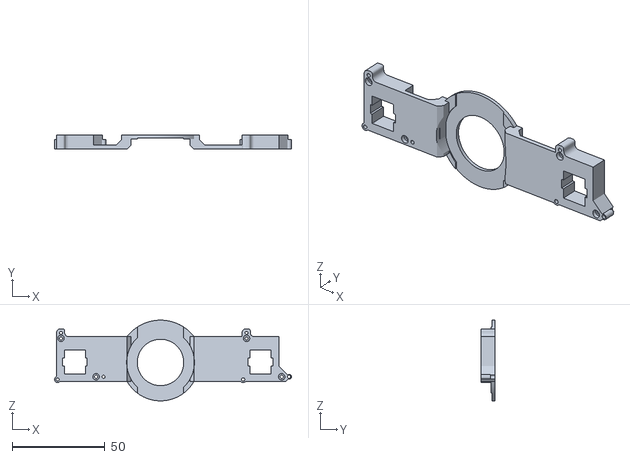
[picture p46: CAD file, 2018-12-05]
CAD/ASSEMBLY_XYZ-STAGE_v0/STL/Assembly_XYZ_Stage_40_XY_Stage_Sample_Adapter_20.stl
127.7 x 7.50 x 43.5

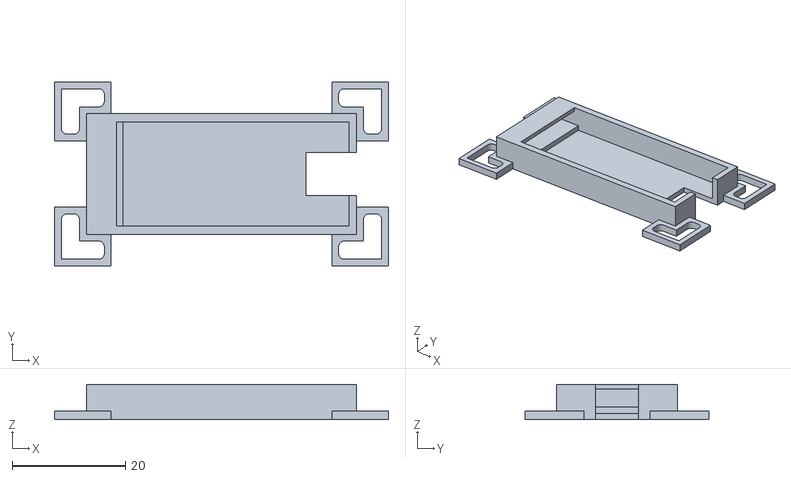
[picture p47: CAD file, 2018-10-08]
CAD/EXT_ELECTRONICS-Mount/STL/Assembly_Electronics_70_Electronics_Mount_Arduino_3.stl
58.9 x 32.5 x 6.20

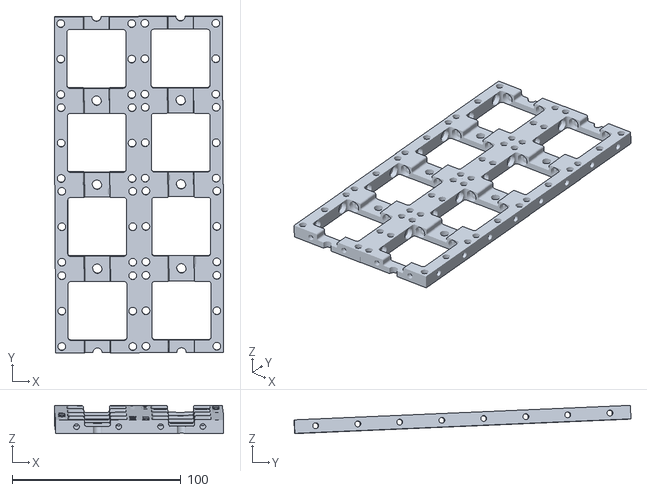
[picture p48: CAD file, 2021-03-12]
MDK/CAD/ALTERNATIVE_DESIGN/UC2_with_3-holes-cubes/STL/Assembly_3h_cube_baseplate_4x2.stl
100.2 x 199.6 x 16.8

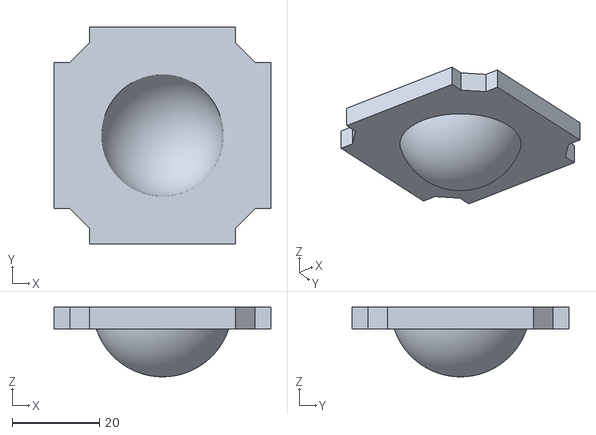
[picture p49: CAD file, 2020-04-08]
TheBOX/CourseBOX/BUILD_ME/STL/32_Assembly_Cube_Eyeball_v2_20_Cube_Insert_Eye_1.stl
49.8 x 49.8 x 16.0

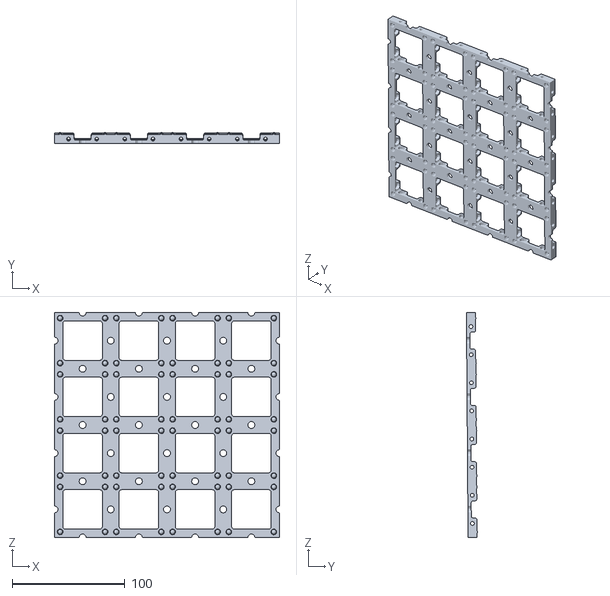
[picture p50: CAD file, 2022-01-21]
WORKSHOP/MAKE_LIGHT_SHEET/ASSEMBLY_Baseplate_v2/STL/Assembly_Cube_Baseplate_4x4_v2.stl
200.0 x 9.94 x 200.1

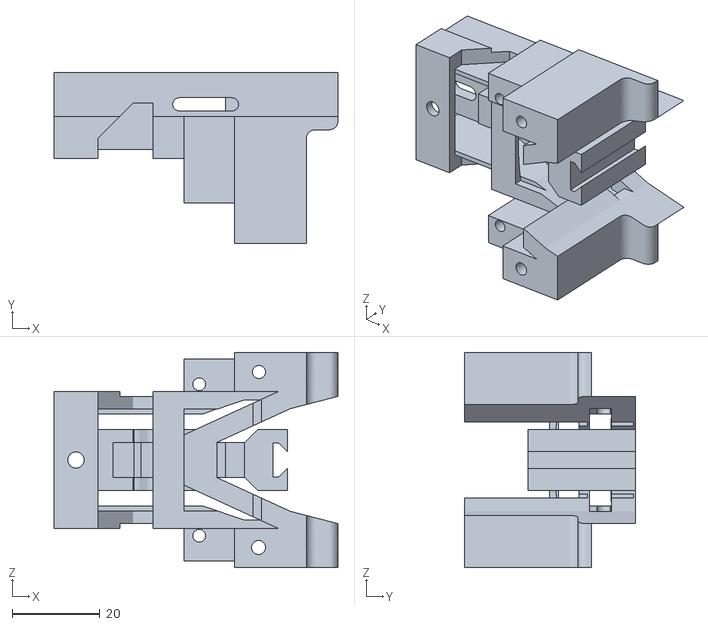
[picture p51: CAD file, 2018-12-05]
CAD/ASSEMBLY_XYZ-STAGE_v0/STL/Assembly_XYZ_Stage_20_Inlet_Focus_U_v2_8.stl
64.7 x 39.0 x 49.0

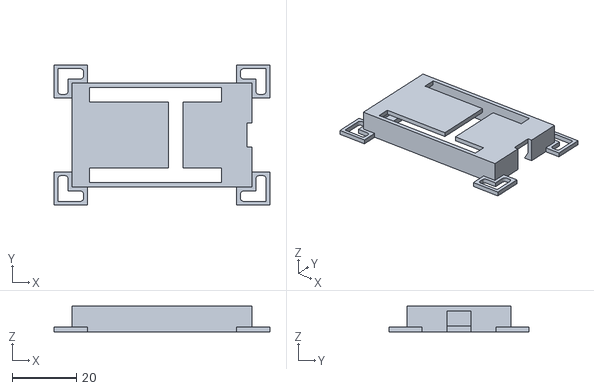
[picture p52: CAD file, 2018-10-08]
CAD/EXT_ELECTRONICS-Mount/STL/Assembly_Electronics_70_Electronics_ESP32_2.stl
67.2 x 43.7 x 8.00

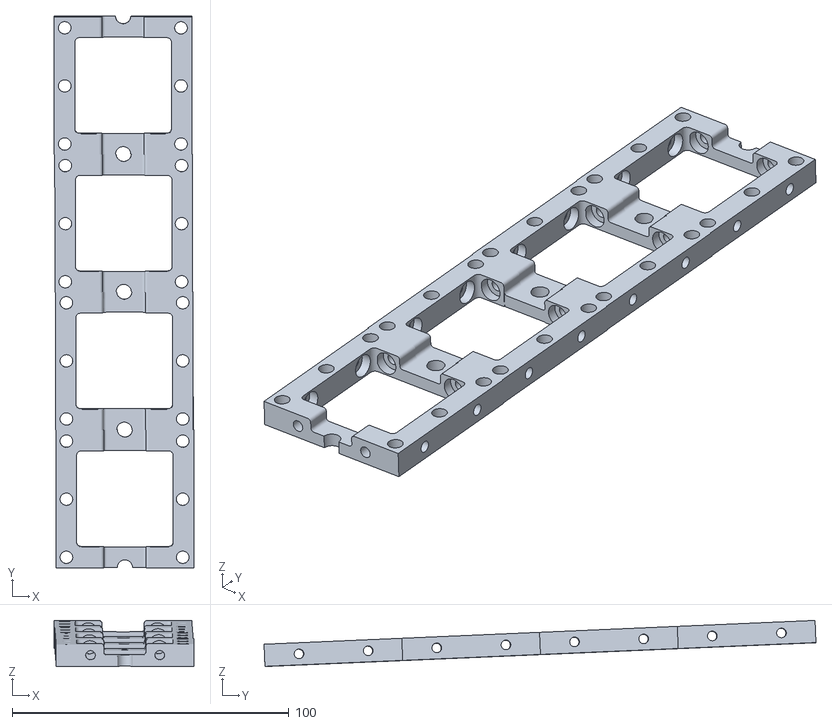
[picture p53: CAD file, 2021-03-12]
MDK/CAD/ALTERNATIVE_DESIGN/UC2_with_3-holes-cubes/STL/Assembly_3h_cube_baseplate_4x1.stl
50.4 x 199.4 x 16.7

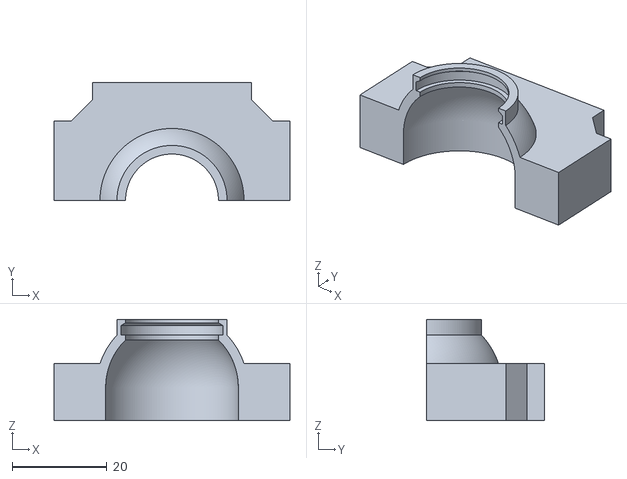
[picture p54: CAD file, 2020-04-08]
TheBOX/CourseBOX/BUILD_ME/STL/33_Assembly_Cube_Eyeball_v2_20_Cube_Insert_Eye_Lens_2.stl
49.8 x 24.9 x 21.3

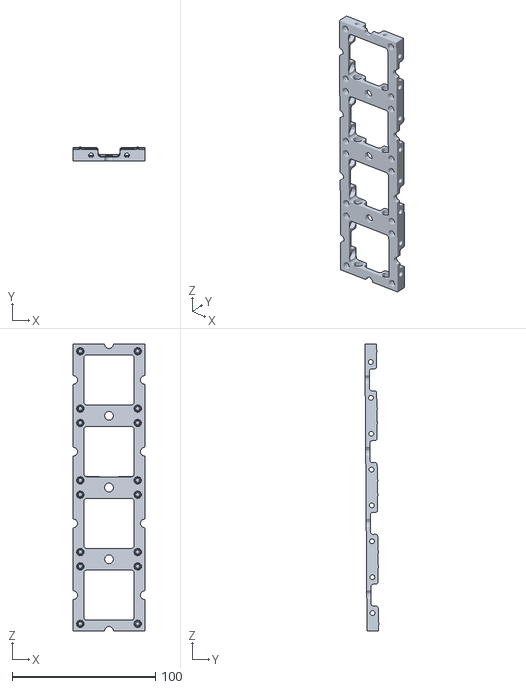
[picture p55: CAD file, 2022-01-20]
WORKSHOP/MAKE_LIGHT_SHEET/ASSEMBLY_Baseplate_v2/STL/Assembly_Cube_Baseplate_4x1_v2.stl
50.0 x 9.94 x 200.1

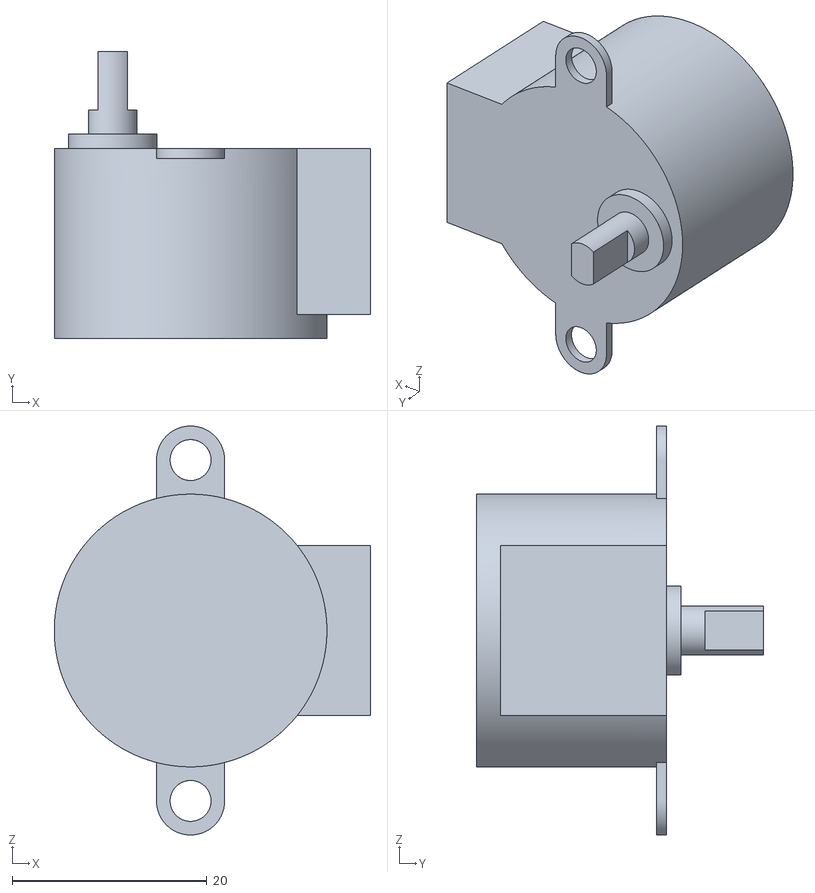
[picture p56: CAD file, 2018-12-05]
CAD/ASSEMBLY_XYZ-STAGE_v0/STL/Assembly_XYZ_Stage_28BYJ-48_4.stl
32.5 x 29.5 x 42.0

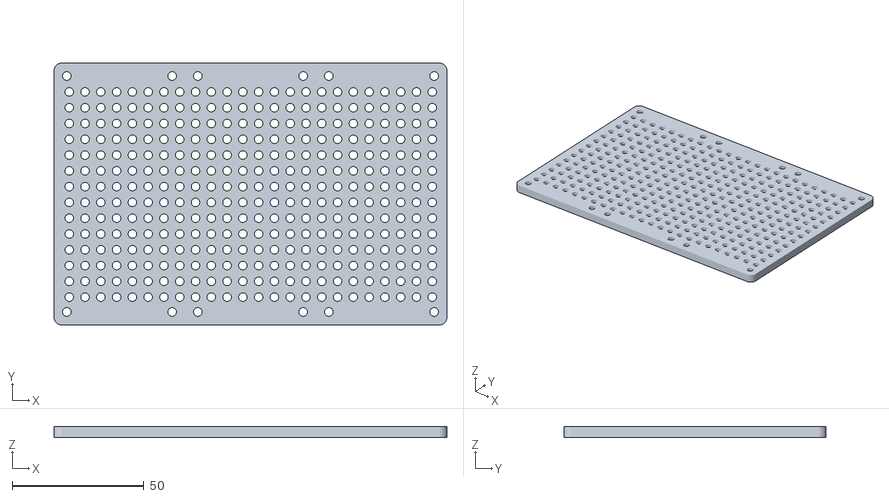
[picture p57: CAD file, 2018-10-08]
CAD/EXT_ELECTRONICS-Mount/STL/Assembly_Electronics_70_Electronics_Baseplate_1.stl
149.4 x 99.6 x 4.00

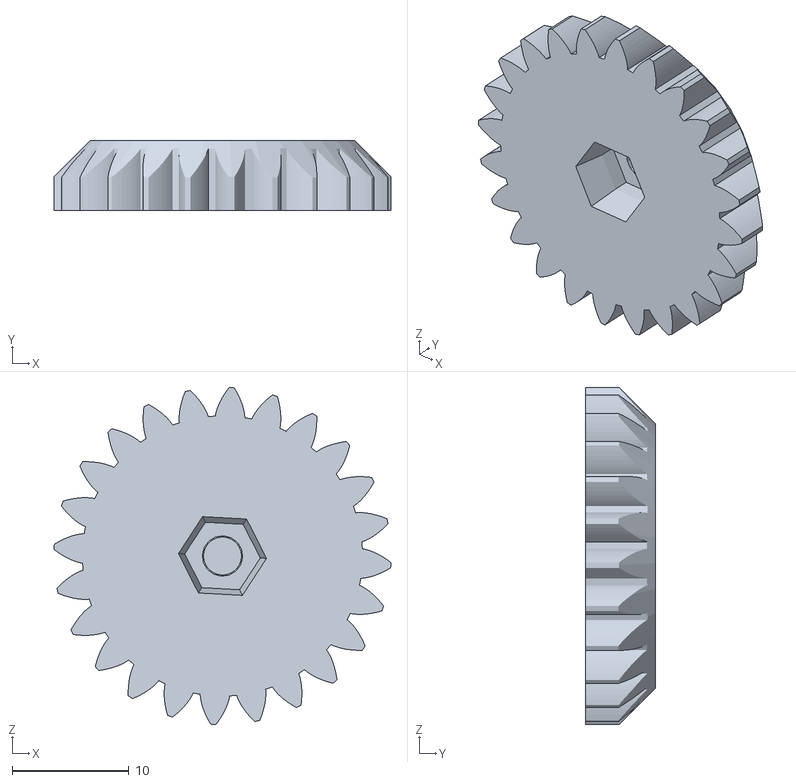
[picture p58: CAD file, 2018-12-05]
CAD/ASSEMBLY_XYZ-STAGE_v0/STL/Assembly_XYZ_Stage_00_large_gear_6.stl
28.9 x 6.00 x 28.9

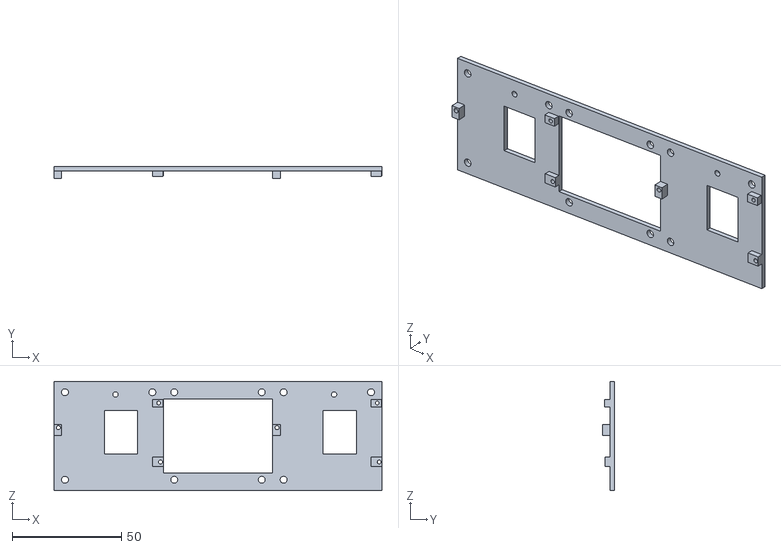
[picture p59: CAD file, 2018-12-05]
CAD/ASSEMBLY_XYZ-STAGE_v0/STL/Assembly_XYZ_Stage_40_XY_Stage_Adapterplate_11.stl
150.0 x 5.50 x 50.0

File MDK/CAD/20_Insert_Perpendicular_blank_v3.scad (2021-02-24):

//Cube insert: Perpendicular 
// Is this insert for a 3D printed cube or for a cube produced by injection molding?
3D_printed_cube = "IM"; // [IM, 3Dprint]

/* [Hiden] */
$fn = 80;
eps = .002;
a = 49.8;
b = 33.6;
c = 6.28;
d = 53.8;
h = 5;
IM_offset = 3D_printed_cube == "3Dprint" ? 0 : 0.2;

insert();

module insert() {
    union() {   //basic insert design
            cube([a,b+2*IM_offset,h], center=true);
            cube([b+2*IM_offset,a,h], center=true);
            rotate(a=[0,0,45]){
                cube([c,d+2*IM_offset,h], center=true);
            }
            rotate(a=[0,0,-45]){
                cube([c,d+2*IM_offset,h], center=true);
            }
        }
}

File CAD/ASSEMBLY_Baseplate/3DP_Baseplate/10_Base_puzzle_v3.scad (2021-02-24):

//Cube insert: Baseplate puzzle piece 

/* [User Parameters] */
//screw offset
scr_offset = 0; //[-0.1:0.1:0.35]
//magnet offset
mag_offset = 0; //[-0.1:0.1:0.35]
//male puzzle offset
puzzle_m_offset = 0; //[0:0.1:0.4]
//female puzzle offset
puzzle_f_offset = 0; //[0:0.1:0.4]


/* [Hiden] */
$fn = 80;
eps = .002;
a = 50; //UC2 unit size
h = 5; //height of the baseplate
b = 34; //size of the inner empty space
mag = 4.85; //magnet hole diameter default
scr = 5.3; //screw hole diameter default
s1 = 10.5; //screw hole to side distance 1 (x,y)
s2 = 4.2; //screw hole to side distance 2 (x,y)
r1 = 2; //radius of fillets
m6_1 = 5; //hole for M6 screw diameter
m6_2 = 8; //hole for M6 screw head diameter
m6_3 = 3; //hole for M6 screw head depth
m6_4 = 4; //hole for M6 screw to side distance
puzz1 = 10; //puzzle protrusion neck thickness
puzz2 = 1.5; //puzzle protrusion neck length
puzz3 = 0.5; //puzzle protrusion distance 3
puzz4 = 0.075; //male to female puzzle protrusion offset 
puzz5 = 0.41; //puzzle protrusion radius of fillets

baseplate_puzzle ();

module baseplate_puzzle () {
    difference () {
    union () { //four corners together
        corner();
        translate([a,0,0]){rotate([0,0,90]){corner();}}
        translate([0,a,0]){rotate([0,0,270]){corner();}}
        translate([a,a,0]){rotate([0,0,180]){corner();}}
        translate([a/2-puzz1/2,-(r1+puzz2),0]){puzzle_m();} //male puzzle
        translate([-(r1+puzz2),a/2+puzz1/2,0]){rotate([0,0,270]){puzzle_m();}} //male puzzle
    }
    translate([a/2,m6_4,-eps/2]){m6_hole();} //M6 screw hole
    translate([m6_4,a/2,-eps/2]){m6_hole();} //M6 screw hole
    translate([a/2-puzz1/2,a-r1-puzz2,0]){puzzle_f();} //female puzzle
    translate([a-r1-puzz2,a/2+puzz1/2,0]){rotate([0,0,270]){puzzle_f();}} //female puzzle
    }
}
module corner () {
    union () {
        difference () {
            cube([a/2,a/2,h]);
            difference () { //outer corner fillet
                translate([-eps,-eps,-eps/2]){cube([r1,r1,h+eps]);}
                translate([r1,r1,-eps/2]){cylinder(h+2*eps,r=r1);}
            }
            translate([(a-b)/2,(a-b)/2,-eps/2]){cube([b/2+eps,b/2+eps,h+eps]);}
            translate([h,h,-eps/2]){cylinder(h+eps,d=mag+mag_offset);} //hole for magnet
            translate([s1,s2,-eps/2]){cylinder(h+eps,d=scr+scr_offset);} //hole for snap fit
            translate([s2,s1,-eps/2]){cylinder(h+eps,d=scr+scr_offset);} //hole for snap fit
        }
        translate([(a-b)/2,(a-b)/2,0]){ //inner corner fillet
            difference () {
                translate([-eps,-eps,]){cube([r1,r1,h+eps]);}
                translate([r1,r1,-eps/2]){cylinder(h+2*eps,r=r1);}
            }
        }
    }
}
module m6_hole () {
    union () {
        cylinder(h+eps,d=m6_1);
        translate([0,0,h-m6_3]){cylinder(m6_3+eps,d=m6_2);}
    }
}
module puzzle_m () {
    union () {
        cylinder(h+eps,r=r1-puzzle_m_offset);
        translate([puzz1,0,0,]){cylinder(h,r=r1-puzzle_m_offset);}
        translate([0,-r1+puzzle_m_offset,0]){cube([puzz1,2*(r1-puzzle_m_offset),h]);}
        translate([puzzle_m_offset,r1-puzzle_m_offset,0]){cube([puzz1-2*puzzle_m_offset,puzz2+puzzle_m_offset,h]);}
        translate([puzz1-puzzle_m_offset,r1-puzzle_m_offset,0]){difference () {
                translate([-eps,-eps,0]){cube([puzz3,puzz3,h]);}
                translate([puzz3,puzz3,-eps/2]){cylinder(h+eps,r=puzz3);}
            }}
        translate([puzzle_m_offset,r1-puzzle_m_offset,0]){rotate([0,0,90]){difference () {
                translate([-eps,-eps,0]){cube([puzz3,puzz3,h]);}
                translate([puzz3,puzz3,-eps/2]){cylinder(h+eps,r=puzz3);}
            }}}
    }
}
module puzzle_f () {
    union () {
        cylinder(h+eps,r=r1+puzz4+puzzle_f_offset);
        translate([puzz1,0,-eps/2]){cylinder(h+eps,r=r1+puzz4+puzzle_f_offset);}
        translate([0,-r1-puzz4-puzzle_f_offset,-eps/2]){cube([puzz1,2*(r1+puzz4+puzzle_f_offset),h+eps]);}
        translate([-1.25*puzzle_f_offset,r1+puzz4+puzzle_f_offset,-eps/2]){cube([puzz1+2*puzz4+2*puzzle_f_offset,puzz2,h+eps]);}
        translate([puzz1+2*puzz4+0.75*puzzle_f_offset,r1+0.5*puzz4+0.75*puzzle_f_offset,0]){difference () {
                translate([-eps,-eps,-eps/2]){cube([puzz5,puzz5,h+eps]);}
                translate([puzz5,puzz5,-eps/2]){cylinder(h+2*eps,r=puzz5);}
            }}
        translate([puzz4-1.5*puzzle_f_offset,r1-puzz4+1.25*puzzle_f_offset,0]){rotate([0,0,90]){difference () {
                translate([-eps,-eps,-eps/2]){cube([puzz5,puzz5,h+eps]);}
                translate([puzz5,puzz5,-eps/2]){cylinder(h+2*eps,r=puzz5);}
            }}}
    }
}

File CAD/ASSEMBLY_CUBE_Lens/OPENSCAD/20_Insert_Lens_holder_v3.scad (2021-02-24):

//Cube insert: Lens holder with clamp 

/* [User Parameters] */
//Lens diameter - measure the diameter of your lens carefully and insert the value in millimetres. The holder can be used for lenses with a diameter from 9 mm to 42 mm.
lens_diameter = 25.4; //[9:0.01:42]
//Edge thickness - measure the thickness of your lens as close to the outer edge as possible.
lens_edge_thickness = 1.5; //[0.5:0.01:8]
// Which part would you like to print?
part = "first"; // [first:Both - Holder AND Clamp,second:Holder ONLY,third:Clamp ONLY]
// Write the focal length of the lens that you will put in this holder. Input: number in millimetres, no units, add '-' for a negative lens. 
focal_length = "f"; 

/* [Hiden] */
$fn = 80;
eps = .002;
a = 49.8;
b = 33.6;
c = 6.28;
d = 53.8;
h = lens_edge_thickness < 4.1 ? 5 : 5+(lens_edge_thickness-3); //holder height
h1 = 3; //clamp rims height
t = 1.5; //clamp ring thickness
IM_offset = 0.2;

print_part();

module print_part() {   //choose part to print holder/clamp/both
	if (part == "first") {
		lens_holder();
        lens_clamp();
	} else if (part == "second") {
		lens_holder();
	} else if (part == "third") {
		lens_clamp();
	} 
}

module lens_holder () {
    difference(){
        union() {   //basic insert design
            cube([a,b+2*IM_offset,h], center=true);
            cube([b+2*IM_offset,a,h], center=true);
            rotate(a=[0,0,45]){
                cube([c,d+2*IM_offset,h], center=true);
            }
            rotate(a=[0,0,-45]){
                cube([c,d+2*IM_offset,h], center=true);
            }
        }
        union() {
            cylinder(h+eps,d=lens_diameter-2, center = true); //hole
            translate([0,0,(h-lens_edge_thickness)/2]){
                cylinder(lens_edge_thickness+eps,d=lens_diameter+0.7, center = true); //rim to hold the lens
            }
        }
        translate([0,-24,((h+h1-0.1)/2-2.45)]){
            linear_extrude(height = 2) text(focal_length, size=5, font="Arial black:style=Regular",halign = "center", spacing=1);
            translate([(lens_diameter+2.9)/2+1,a/2-1,0]){cube([3,1,2+eps], center = true);}
            translate([-1,(a+lens_diameter+2.9)/2+1,0]){cube([1,3,2+eps], center = true);}
            translate([1,(a+lens_diameter+2.9)/2+1,0]){cube([1,3,2+eps], center = true);}
        }
    }
    translate([0,0,(h+h1-0.1)/2]){  //rim for the clamp
        scale([1,1.03,1])difference(){
                cylinder(h1+0.1,d=lens_diameter+2.9, center = true);  
                cylinder(h1+0.1+eps,d=lens_diameter+0.7, center = true);
        }
    }
}

module lens_clamp() {
    translate([a/2+lens_diameter/2+7,0,-(h-t)/2]){
        scale([1,1.03,1])difference(){   //bottom ring
            cylinder(t, d=lens_diameter+4.9, center = true);
            cylinder(t+eps, d=lens_diameter-1, center = true);
        }
        translate([0,0,+(h1+t)/2]){
            scale([1,1.03,1])difference(){   //outer rim
                cylinder(h1,d=lens_diameter+4.9, center = true);
                cylinder(h1+eps,d=lens_diameter+2.9, center = true);
            }
            scale([1,1.03,1])difference(){   //inner rim
                cylinder(h1,d=lens_diameter+0.5, center = true);
                cylinder(h1+eps,d=lens_diameter-1, center = true);
                }
            }
        translate([(lens_diameter+4.9)/2,0,-t/2]){cylinder(t+h1,2,2,$fn=3);}
        }
    }

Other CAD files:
CAD/ASSEMBLY_XYZ-STAGE_v0/STL/Assembly_XYZ_Stage_10_Cube_2x_v0_1.stl
CAD/ASSEMBLY_XYZ-STAGE_v0/STL/Assembly_XYZ_Stage_05__RMS_Adapter_v2_5.stl
CAD/ASSEMBLY_XYZ-STAGE_v0/STL/Assembly_XYZ_Stage_10_Cube_TRI_v0_13.stl
CAD/ASSEMBLY_XYZ-STAGE_v0/STL/Assembly_XYZ_Stage_00_small_gear_7.stl
APPLICATIONS/APP_POL_Newtons_Rings_Experiment/STL/20_Cube_Insert_Beamexpander_astromedia_v3.stl
CAD/APP_Double-slit_Experiment/STL/10_Cube_1x1_v2.stl
CAD/APP_Double-slit_Experiment/STL/10_Lid_1x1_v2.stl
CAD/APP_INLINE_HOLOGRAM/STL/10_Cube_1x1_v2.stl
CAD/APP_INLINE_HOLOGRAM/STL/10_Lid_1x1_v2.stl
CAD/APP_SIMPLE-Projector/STL/10_Cube_1x1_v2.stl
CAD/APP_SIMPLE-Projector/STL/10_Lid_1x1_v2.stl
CAD/APP_SIMPLE-Telescope/STL/10_Cube_1x1_v2.stl
CAD/APP_SIMPLE-Telescope/STL/10_Lid_1x1_v2.stl
CAD/ASSEMBLY_CUBE_ArduCamUSB/STL/20_Cube_Insert_Arducam_USB_insert_v3.ipt
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

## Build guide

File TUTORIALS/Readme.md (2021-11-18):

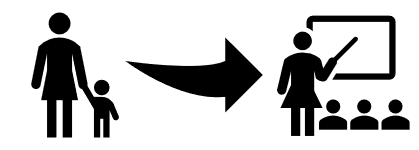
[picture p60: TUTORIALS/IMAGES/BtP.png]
#  From a Beginner to a Professional

... in clear and simple steps! Here you find guidelines that will lead you through the UC2 toolbox.

If you're searching for a specific topic, have a look through the points below - maybe your question was already answered. If not, you can always file an issue or contact us!

Feel free to skip to the steps that you're most interested in - and feel free to jump back to the basics if you feel like you missed out something.

All external links are used with the best intention - to provide more information and background on topics that are not in our main focus.

##  First steps

#### GitHub
[What is GitHub? How to join?](https://guides.github.com/activities/hello-world/)  
[How to access all the files easily?](https://help.github.com/en/github/creating-cloning-and-archiving-repositories/cloning-a-repository)  
[How to make your First Contribution?](https://firstcontributions.github.io/)  
[How to make your First Contribution if the previous guide still seems to complicated?](https://github.com/firstcontributions/first-contributions/)  
[How to edit GitHub documentation (Readme files)?](https://atom.io/)  
[How to use GitHub flavored Markdown?](https://help.github.com/en/github/writing-on-github/basic-writing-and-formatting-syntax)

#### Shopping for material and components
[What do I have to buy if I want to build something with UC2 toolbox?](./RESOURCES/Resources_step_by_step.md)  
[Is there a complete list of all setups, modules and components?](https://docs.google.com/spreadsheets/d/1U1MndGKRCs0LKE5W8VGreCv9DJbQVQv7O6kgLlB6ZmE/edit?usp=sharing)

#### 3D printing
[Never tried it but it's so cool you want to start now?](https://www.makeuseof.com/tag/beginners-guide-3d-printing/)  
[Which printer do we mostly use?](https://www.prusa3d.com/original-prusa-i3-mk3/)  
[I don't have a 3D printer. Can I have the parts printed somewhere in Jena?](https://lichtwerkstatt-jena.de/)  
[I don't have a 3D printer. Where can I have them printed?](https://www.makerspaces.com/what-is-a-makerspace/)  

#### Injection moulded (IM) or 3D-printed cubes (3DP)?
[Which cubes are the most up-to-date ones?](../MDK#uc2-version-history)  
[What is the difference between IM and 3DP cubes?](..CAD/ASSEMBLY_CUBE_Base)  
[How do the baseplate puzzles work?](../ASSEMBLY_Baseplate)  

#### Electronics
[Which software do I need to control the electronic components?](https://randomnerdtutorials.com/installing-the-esp32-board-in-arduino-ide-windows-instructions/)    
[How to solder electronics?](https://www.makerspaces.com/how-to-solder/)  
[How to avoid soldering?](../ELECTRONICS/ELECTRONICS_FOR_DUMMIES)

#### Handling Optics
Even if you don't aim for research application of the setups -handle the optical components with care, protect them from dust and avoid fingerprints on optical surfaces.    
[How to handle optics?](https://www.thorlabs.com/newgrouppage9.cfm?objectgroup_id=9025)  
[How to clean dirty optics?](https://www.newport.com/n/how-to-clean-optics)  

#### Software
[Where do I find all the UC2-Software documentation in one place?](https://github.com/bionanoimaging/UC2-Software-GIT)  
[How to prepare the hardware of the Raspberry Pi?](https://www.techcoil.com/blog/how-to-setup-the-raspberry-pi-official-7-inch-touch-screen-with-your-raspberry-pi-4-model-b/)  
[How to start with Raspberry Pi?](https://projects.raspberrypi.org/en/projects/raspberry-pi-setting-up)  

##  Tutorials

Tutorials take you by hand through your beginnings with UC2. It's useful to get familiar with the cubes before starting building a more complex system.  
Check the [RESOURCES](./RESOURCES/Resources_step_by_step.md) you will need to accomplish the tutorials.  
Choose whether you prefer a :feet: Step-by-Step tutorial with images or a :movie_camera: YouTube Video

* TUT01: Print your first cube [:feet:](../CAD/ASSEMBLY_CUBE_Base/STL) [:movie_camera:](https://www.youtube.com/watch?v=SblqYJYXe4k&feature=youtu.be)
* TUT02: Assemble your first cube [:feet:](../CAD/ASSEMBLY_CUBE_Base#assembly) [:movie_camera:](https://www.youtube.com/watch?v=zAMedY0mWKA&t=1s)
* TUT03: Give your first cube a function - lens as a magnifying glass [:feet:](../CAD/ASSEMBLY_CUBE_Lens/TUT03)
* TUT04: Build your first baseplate [:feet:](../CAD/ASSEMBLY_Baseplate)[:movie_camera:](https://www.youtube.com/watch?v=qxA-4V7BRI0)
* TUT05: Build your first optical setup - a telescope [:feet:](../APPLICATIONS/APP_SIMPLE-Telescope)
* TUT06: Build your first microscope [:feet:](../APPLICATIONS/APP_SIMPLE-Smartphone_Microscope/mechanical)
* TUT07: Get your first electronic part - simple LED matrix [:feet:](../CAD/ASSEMBLY_CUBE_LED_Matrix_simple)
* TUT08: Build your first microscope with electronics [:feet:](../APPLICATIONS/APP_SIMPLE-Smartphone_Microscope/electronic)
* TUT09: Build your first BOX [:feet:](../TheBOX/SimpleBOX/BUILD_ME)
* TUT10: Explore optics with your first BOX [:feet:](../TheBOX/SimpleBOX/USE_ME)[:movie_camera:](https://www.youtube.com/watch?v=glL_bdoeETM&t=2s&ab_channel=openUC2)

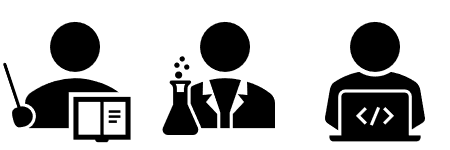
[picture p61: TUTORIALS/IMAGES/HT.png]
##  How-to guides
How-to guides show you how to assemble cubes for various functions and how to build many different optical setups, once you are familiar with the basic idea. It also takes you from the mechanical-only to motorized systems.

* [HOW-TO find all the cubes and components](../CAD)
* [HOW-TO assemble cubes for different functions](../CAD)
* [HOW-TO find optical setups that are already tested](../APPLICATIONS)
* [HOW-TO set up a Raspberry Pi for the use in UC2 toolbox](https://github.com/bionanoimaging/UC2-Software-GIT/blob/master/GUI/RASPBERRY_PI/README.md)
* [HOW-TO print the UC2 parts with a *Prusa i3 MK3S* Printer](./PRINTER)
* [HOW-TO import your ideas into the UC2 framework](../MDK)
* [HOW-TO easily sketch your UC2 setups](../MDK/DRAW.IO)
* [HOW-TO work with the MiniBOX](../TheBOX/SimpleBOX/USE_ME)
* HOW-TO use UC2 toolbox for education?
* HOW-TO use UC2 toolbox for research?

##  Contributor guidelines

We appreciate that you want to get involved! Your help is valuable for us, even if you are not a skilled researcher, maker or programmer. These are mostly guidelines, not rules. Use your best judgment, and feel free to propose changes to this document in a pull request.

Find the detailed guidelines in [CONTRIBUTING](../CONTRIBUTING.md)

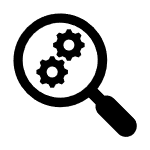
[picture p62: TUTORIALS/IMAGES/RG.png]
##  Reference guides
Reference guides give you more information on specific topics and provide technical details.  
Find out more about...

* [REF: Open-Source](https://opensource.org/)
* [REF: Open-hardware](https://www.oshwa.org/)
* REF: Learn more about Optics and Microscopy: [MicroscopyU](https://www.microscopyu.com/), [YT Microcourses](https://www.youtube.com/channel/UC4cOKa0TZK8CQhzSQqfwuMQ), [YT Optical Systems](https://www.youtube.com/channel/UCI3DnTADGjHCuuaLr3LHf8A/videos)
* [REF: Electronics](../ELECTRONICS)
* [REF: Soldering -learn more](https://learn.sparkfun.com/tutorials/how-to-solder-through-hole-soldering/all)
* [REF: Arduino](https://www.arduino.cc/en/guide/introduction)
* [REF: ESP32](https://www.espressif.com/en/products/hardware/esp32/overview)
* [REF: Raspberry Pi](https://www.raspberrypi.org/documentation/)
* [REF: 3D printing material: PLA](https://www.creativemechanisms.com/blog/learn-about-polylactic-acid-pla-prototypes)
* [REF: 3D printing material: ABS](https://www.creativemechanisms.com/blog/everything-you-need-to-know-about-abs-plastic)
* [REF: Datasheets](./DATASHEETS)
* More links in [Resources: Knowledge](./RESOURCES/Resources_Knowledge.md)
* _Alternative Unit Block Designs_ : The UC2 cubes and baseplate system from some instability coming from the  4-point attachment design, as this is an over-determined connection. We tried other designs that should in theory be better. But what they were?

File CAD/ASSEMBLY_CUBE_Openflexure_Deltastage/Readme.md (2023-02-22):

# Cube Insert OpenFlexure (Delta) Stage
This part adapts the OpenFlexure Delta-stage from Richard Bowman's group at the Bath University to the modular optical system UC2. It is basically a plate which has  4 ball-magnets on one side to adapt to 1 UC2 cubes and a flat surface equipped with 3 holes to adapt to the openflexure delta-stage.

Please have a look here for an updated version of the adapter: https://github.com/openUC2/UC2-OpenFlexureStage

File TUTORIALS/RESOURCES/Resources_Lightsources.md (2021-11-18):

## Resources: Lasers and Light sources

We cannot guarantee the availability of the components. If you know other components, please let us know by filing an issue. Thank you :-)

### Lasers
|  Name | Properties  |  Price | Link  | Tested |
|---|---|---|---|---|
|  Unknown | SINGLE MODE, 638NM, 120MW ORANGE RED  | 20€  | [Laserlands](https://www.laserlands.net/)  | Yes |
Unknown | 5mW 450nm Blue Laser Pointer Pen | 15€ | [Laserlands](https://www.laserlands.net/11040037.html) | Yes
Unknown | 1668 450nm 80mW Blue Laser Dot Module | 22€ | [Laserlands](https://www.laserlands.net/diode-laser-module/445-473nm-blue/11041055.html) | Yes
Protective goggles | LP-GTY 200nm-532nm OD6+ 900n-1100nm OD5+ Laser Protective Goggles Safety Glasses | 28€| [Laserlands](https://www.laserlands.net/protection/laser-glasses/laserland/200nm-532nm-od6-900n-1100nm-od5-laser-protective-goggles-safety-glasses.html) | Yes
Unknown | Heavy duty lasers (can be ordered from University!) | 25-100€ | [prolasersysetems](https://www.prolasersystems.com/laserman-systeme/) | Yes
Unknown | Heavy duty lasers (can be ordered from University!) | 25-100€ | [MQuadrat Laser](https://www.prolasersystems.com/laserman-systeme/) | Yes
Unknown | Heavy duty lasers (can be ordered from University!) | 25-100€ | [roithner](http://www.roithner-laser.com/) | Yes
|  Unknown | Everything you want! (Diodes, Drivers, Lenses)  | 1-200€  | [dtrslasershop](https://sites.google.com/site/dtrslasershop/home/laser-drivers)  | No
Ansmann Laser pointer | 2in1 red laser pointer and white LED | 5 € |[Conrad electronics](https://www.conrad.de/de/p/ansmann-laserpointer-2in1-reichweite-max-im-freifeld-50-m-2162622.html)|Yes
|  Micost Optotech | All kind of laser sources (also fiber coupled)  | >20€  | [Micost Optotech](http://www.micost-optotech.com/products.asp?did=94&xid=96)  | Yes |
|  Roithner Laser | All kind of laser sources (also fiber coupled)  | >200€  | [Roithner Laser](http://www.roithner-laser.com/ld_fiber.html)  | Yes |
|  Lasertack GmbH | High quality lasers at low prices made in Germany | >200€  | [Lasertack (Kassel, GER)](https://www.lasertack.com/en/55mw-488nm-laser-diode)  | No |

Nice. There is also: Reutner (Österreich)und und Marco Lauschmann mit MQuadrat Laser

We highly recommend you to check the marketing with known retailers (e.g. eBay, Amazon, Aliexpress, Alibaba). We made good experience with the low-cost optics!

### LEDs
|  Name | Properties  |  Price | Link  |
|---|---|---|---|
| Power LEDs  |  Various |  1-5 € | [Amazon](https://www.amazon.de/Haobase-5Stk-Power-weiss-Licht/dp/B01EW79IPY/ref=sr_1_1?ie=UTF8&qid=1542894544&sr=8-1&keywords=power+led+star)  |
Hi-Power LED STAR | 1W/3W UV | 2€ | [Ebay](https://www.ebay.de/itm/Hi-Power-LED-1W-3W-UV-STAR-Ultraviolet-/131326525056?var=) | Yes
LED ring | 40 mm / 50 mm / 70 mm / 80 mm / 100 mm 40 mm | 8-10€ |[Amazon](https://www.amazon.de/dp/B07ML3PTYS/ref=pe_3044161_185740101_TE_item)
LED matrix | 8×8, AZ delivery | 10€ | [Amazon](https://www.amazon.de/AZDelivery-Matrix-CJMCU-8-Arduino-Raspberry/dp/B078HYP681/ref=sr_1_2?__mk_de_DE=%C3%85M%C3%85%C5%BD%C3%95%C3%91&keywords=neopixel+matrix&qid=1565008576&s=gateway&sr=8-2) | Yes
LED matrix | 8×8, AZ delivery | 12€ | [AZ delivery](https://www.az-delivery.de/products/u-64-led-panel?ls=de) | Yes
LED matrix | 8×8, Neopixel Adafruit | 50€ | [Amazon](https://www.amazon.de/Adafruit-NeoPixel-NeoMatrix-8x8-64-Matrix/dp/B00FA9JDEU) | Yes
Flashlight |LED, Alu, 5 W CREE-LED | 7€ | [pollin.de](https://www.pollin.de/p/led-taschenlampe-alu-5-w-cree-led-864151) | Yes

Other shops are Reichelt, Amazon, RS-Electronics etc. LEDs are a very sensitive part when it comes to spectra. So choose it with care!

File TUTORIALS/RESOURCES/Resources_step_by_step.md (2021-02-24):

# Resources step-by-step

If your planning to get familiar with the toolbox by going through all our [TUTORIALS](../), you need to prepare the following:

### Tools

Tool             |  Image|  Comment
:-------------------------:|:----------------------------:|:-------------------------:
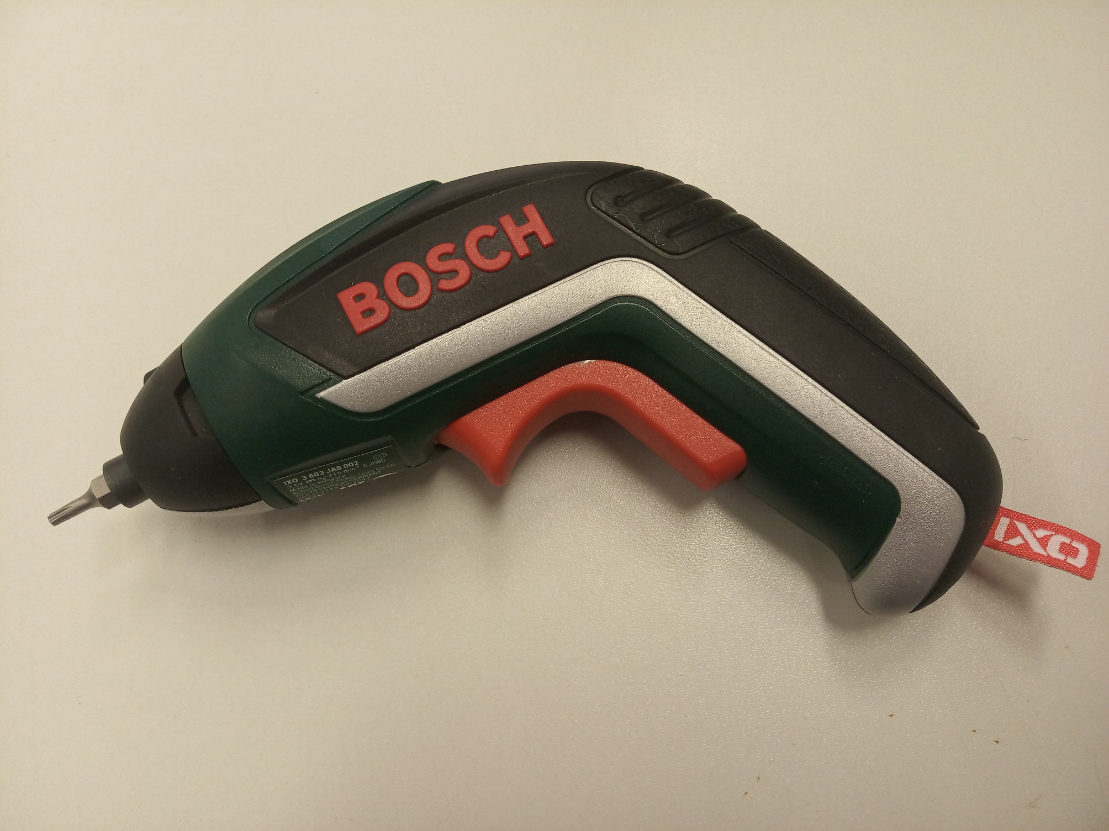
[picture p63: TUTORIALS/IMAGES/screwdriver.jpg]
[Electric screw driver with 2,5 mm hex bit](https://www.amazon.de/Bosch-Akkuschrauber-Generation-Bits-Ladeger%C3%A4t/dp/B00TTZU566/ref=asc_df_B00TTZU566/?tag=googshopde-21&linkCode=df0&hvadid=255989693737&hvpos=1o1&hvnetw=g&hvrand=6125749874385941808&hvpone=&hvptwo=&hvqmt=&hvdev=c&hvdvcmdl=&hvlocint=&hvlocphy=9042960&hvtargid=pla-421346020200&psc=1&th=1&psc=1) | | For putting the cubes together using M3×12 screws.
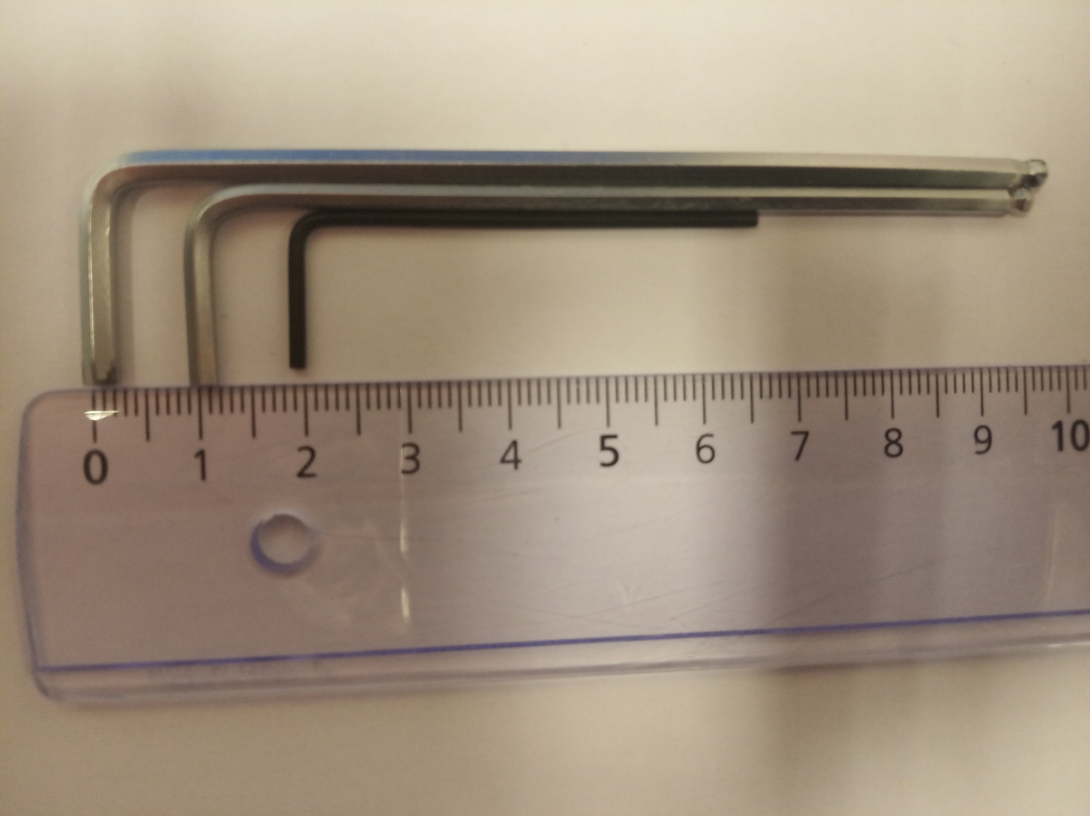
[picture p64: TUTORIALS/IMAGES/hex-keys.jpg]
[2,5 mm hex key](https://www.amazon.de/Presch-Innensechskant-Satz-Kugelkopf-Innensechskantschl%C3%BCssel/dp/B079V335CR/ref=sr_1_2_sspa?__mk_de_DE=%C3%85M%C3%85%C5%BD%C3%95%C3%91&crid=2K89GU3MY8P26&keywords=hex+key+set&qid=1575997133&s=diy&sprefix=hex+%2Cdiy%2C160&sr=1-2-spons&psc=1&spLa=ZW5jcnlwdGVkUXVhbGlmaWVyPUEzRENMU0hKWkJRR0FEJmVuY3J5cHRlZElkPUEwMDIzMjIyMzFBWVIyOEpORU1FSCZlbmNyeXB0ZWRBZElkPUEwMzk0NjQwMlA0NFZDTVk0Tk9LUSZ3aWRnZXROYW1lPXNwX2F0ZiZhY3Rpb249Y2xpY2tSZWRpcmVjdCZkb05vdExvZ0NsaWNrPXRydWU=) | | For fine adjustment of all the M3 screws if needed.
[1,5 mm hex key](https://www.amazon.de/Presch-Innensechskant-Satz-Kugelkopf-Innensechskantschl%C3%BCssel/dp/B079V335CR/ref=sr_1_2_sspa?__mk_de_DE=%C3%85M%C3%85%C5%BD%C3%95%C3%91&crid=2K89GU3MY8P26&keywords=hex+key+set&qid=1575997133&s=diy&sprefix=hex+%2Cdiy%2C160&sr=1-2-spons&psc=1&spLa=ZW5jcnlwdGVkUXVhbGlmaWVyPUEzRENMU0hKWkJRR0FEJmVuY3J5cHRlZElkPUEwMDIzMjIyMzFBWVIyOEpORU1FSCZlbmNyeXB0ZWRBZElkPUEwMzk0NjQwMlA0NFZDTVk0Tk9LUSZ3aWRnZXROYW1lPXNwX2F0ZiZhY3Rpb249Y2xpY2tSZWRpcmVjdCZkb05vdExvZ0NsaWNrPXRydWU=) |↑↑ | For M2 screws.

### Additional components organized by Tutorials
The parts add on - for the later step you mostly need all the components from the previous ones. On the other hand, the cube get reused in the later steps - we recommend to carefully read through the tutorials before buying the components.

#### TUT01: Print your first cube

  Name | Properties  | Amount|  Price | Link  | Tested
---|---|---|---|---|---
3D printing material (PLA, ABS)|Choose the material that works with your printer, but rather don't go for the cheapest, it does make a difference||30-60€ / kg||

#### TUT02: Assemble your first cube
The IM Cube doesn't need any additional components.  
For the 3DP Cube, you will need lots and lots of screws!

Name | Properties  | Amount|  Price | Link  | Tested
---|---|---|---|---|---
Screws M3×12|DIN912, cylindrical, galvanized steel - magnetic!|8 per Cube Base|13€ / 500 pieces|[Würth](https://eshop.wuerth.de/Zylinderschraube-mit-Innensechskant-SHR-ZYL-ISO4762-88-IS25-A2K-M3X12/00843%20%2012.sku/de/DE/EUR)|Yes
Screws M3×8|DIN912, cylindrical, galvanized steel - magnetic!|We use 4×12 mm screws to attach the lid and 4×8 mm screws on the other side, but you can use just M3×12. |13€ / 500 pieces|[Würth](https://eshop.wuerth.de/Zylinderschraube-mit-Innensechskant-SHR-ZYL-ISO4762-88-IS25-A2K-M3X8/00843%20%208.sku/de/DE/EUR/)|Yes
Set screws M5×8 | Galvanized steel, hexagon socket |6 per Cube Base | 15€ / 500 pieces | [Würth](https://eshop.wuerth.de/Produktkategorien/ISO-4026-Stahl-45H-verzinkt/14013511052004.cyid/1401.cgid/de/DE/EUR/?CatalogCategoryRef=14013511052004%40WuerthGroup-Wuerth-1401&SelectedFilterAttribut=%255B%257B%2522name%2522%253A%2522AT_ThreadTypeXNominalDiameter%2522%252C%2522value%2522%253A%255B%2522M5%2522%255D%252C%2522title%2522%253A%2522Gewindeart%2520x%2520Nenndurchmesser%2522%257D%252C%257B%2522name%2522%253A%2522AT_Length%2522%252C%2522value%2522%253A%255B%25228%2520mm%2522%255D%252C%2522title%2522%253A%2522L%25C3%25A4nge%2522%257D%255D) | Yes

**IMPORTANT: Not all screws are magnetic!**  
It is very important to buy the right screws - the M3 screws need to attach to the magnets and therefore it is crucial that they are magnetic. STAINLESS STEEL IS GENERALLY NOT A MAGNETIC MATERIAL. THE SCREWS HAVE TO BE MADE OF GALVANIZED STEEL. If you want to know more about why not all steel is magnetic you can read about it [here](https://monnigindustry.com/2020/12/23/is-galvanized-steel-magnetic-why-or-why-not/). Unfortunately, the DIN 912 / ISO 4762 screws that we propose can be made of both and you can frequently find both at the same vendor.    
The take-home message is: **The M3 screws have be made of galvanized steel and never stainless steel!**

#### TUT03: Give your first cube a function - lens as a magnifying glass
Use the cube you already have and place the lens inside.  
Make sure to print the right holder for the chosen lens!

Name | Properties  | Amount|  Price | Link  | Tested
---|---|---|---|---|---
Planoconvex Lens, *f* = +40 mm, diameter 25,4 mm | Artikel 2120, alternatively you can choose another source and lens with *f* between 30 - 50 mm|1|6 €| [Optikbaukasten](https://optikbaukasten.de/)|Yes
ALTERNATIVE: Bi-convex, *f* = +50 mm, diameter 38 mm | LI150-0050, available from Amazon or directly from [ajaxscientific.com](https://ajaxscientific.com/) | 1 | 10€ | [Amazon](https://www.amazon.com/Ajax-Scientific-Double-Convex-Bi-Convex-Spherical/dp/B00EPQ9EVQ) | Yes

#### TUT04: Build your first baseplate

Name | Properties  | Amount|  Price | Link  | Tested
---|---|---|---|---|---
Ballmagnets | Diameter 5 mm|16 per 4×1 baseplate|0,35 € / piece| [Magnetladen](https://www.magnetladen.de/kugelmagnet-5-mm-n42-nickel/) [Amazon](https://www.amazon.de/COFCO-125-Neodym-Kugelmagnete-5-mm/dp/B076QGPRFF/ref=sr_1_cc_5?s=aps&ie=UTF8&qid=1542899825&sr=1-5-catcorr&keywords=kugelmagnet+5mm)|Yes

#### TUT05: Build your first optical setup - a telescope
Use the lens cube from TUT03 and two baseplates according to TUT04. Above that:

Name | Properties  | Amount|  Price | Link  | Tested
---|---|---|---|---|---
Planoconvex Lens, *f* = +40 mm, diameter 25,4 mm|Artikel 2120, alternatively you can choose another source and lens with *f* = +50 mm, diameter 25,4 mm|1|6 €| [Optikbaukasten](https://optikbaukasten.de/)|Yes
Planoconvex Lens, *f* = +100 mm, diameter 25,4 mm|Artikel 2004|1|6 €| [Optikbaukasten](https://optikbaukasten.de/)|Yes
Planoconvex Lens, *f* = -50 mm, diameter 25,4 mm|LC1259|1|19 €| [Thorlabs](https://www.thorlabs.com/thorproduct.cfm?partnumber=LC1259)|Yes

Make sure to print the right holder for the chosen lenses!   

ALTERNATIVE:

Name | Properties  | Amount|  Price | Link  | Tested
---|---|---|---|---|---
Bi-convex, *f* = +50 mm, diameter 38 mm | LI150-0050, available from Amazon or directly from [ajaxscientific.com](https://ajaxscientific.com/) | 1 | 10€ | [Amazon](https://www.amazon.com/Ajax-Scientific-Double-Convex-Bi-Convex-Spherical/dp/B00EPQ9EVQ) | Yes
Bi-convex, *f* = +100 mm, diameter 38 mm | LI150-0100, available from Amazon or directly from [ajaxscientific.com](https://ajaxscientific.com/) | 1 | 10€ | [Amazon](https://www.amazon.com/Ajax-Scientific-Polished-Spherical-Bi-convex/dp/B00EPQ9GRS) | Yes
Bi-concave, *f* = -50 mm, diameter 38 mm | LI140-0050, available from Amazon or directly from [ajaxscientific.com](https://ajaxscientific.com/) | 1 | 10€ | [Amazon](https://www.amazon.de/-/en/Scientific-LI140-0050-Polished-Spherical-Concave-Diameter/dp/B00EPQ8ZH0) | Yes

#### TUT06: Build your first microscope

Name | Properties  | Amount|  Price | Link  | Tested
---|---|---|---|---|---
Microscope Objective | 4×, RMS thread|1|10 €| [Aliexpress](https://de.aliexpress.com/item/32947647522.html?spm=a2g0x.search0104.3.54.6cf57a4c3DwsTO&transAbTest=ae803_3&ws_ab_test=searchweb0_0%2Csearchweb201602_6_10065_10130_10068_10890_10547_319_10546_317_10548_10545_10696_10084_453_454_10083_10618_10307_537_536_10902_10059_10884_10887_321_322_10103%2Csearchweb201603_6%2CppcSwitch_0&algo_pvid=06d972be-b176-4446-8665-56d9e61a8d2c&algo_expid=06d972be-b176-4446-8665-56d9e61a8d2c-7)|Yes
Eyepiece | 20x, The holder is designed for an eyepiece of this diameter, but in general any eyepiece works. |1; Sold in pairs.|13 €| [Aliexpress](https://de.aliexpress.com/item/32965050204.html?spm=a2g0o.productlist.0.0.7aa657eeefLUfu&algo_pvid=cd60fca0-3fa5-4191-9ce9-303815e2afa7&algo_expid=cd60fca0-3fa5-4191-9ce9-303815e2afa7-1&btsid=76036b58-6717-4d1f-a4a0-c3d4bacd0450&ws_ab_test=searchweb0_0,searchweb201602_2,searchweb201603_52)|Yes
Mirror |30×30 mm², sticker-like|  2; Sold in 45 pieces package |0,50 € / piece| [Amazon](https://www.amazon.de/Rayher-14548606-Spiegelmosaik-selbstklebend-SB-Btl/dp/B008KJ8438/ref=pd_bxgy_201_img_3/258-8761405-4543762?_encoding=UTF8&pd_rd_i=B008KJ8438&pd_rd_r=80fd534c-997b-4a19-b91a-9bf38dbf4ade&pd_rd_w=4DEXV&pd_rd_wg=7SLRE&pf_rd_p=98c98f04-e797-4e4b-a352-48f7266a41af&pf_rd_r=N95R9S45MNSYNQX2BAJE&psc=1&refRID=N95R9S45MNSYNQX2BAJE)| Yes
M3 Screw, 30 mm or longer with M3 Nut|Non-magnetic, for Z-stage|1+1|||
Screws M3×8|For the Z-stage. DIN912, cylindrical, galvanized steel - magnetic!|8 |13€ / 500 pieces|[Würth](https://eshop.wuerth.de/Zylinderschraube-mit-Innensechskant-SHR-ZYL-ISO4762-88-IS25-A2K-M3X8/00843%20%208.sku/de/DE/EUR/)|Yes

#### TUT07: Get your first electronic part - simple LED matrix

Name | Properties  | Amount|  Price | Link  | Tested
---|---|---|---|---|---
LED matrix |Neopixel, 8x8|1|10 €|[Amazon](https://www.amazon.de/AZDelivery-Matrix-CJMCU-8-Arduino-Raspberry/dp/B078HYP681/ref=sr_1_2?__mk_de_DE=%C3%85M%C3%85%C5%BD%C3%95%C3%91&keywords=neopixel+matrix&qid=1565008576&s=gateway&sr=8-2)|Yes
Screws M2 with nuts |Non-magnetic, Alternatively use hot glue|2+2|
ESP32 ||1||[Amazon]((https://www.amazon.de/AZDelivery-NodeMCU-Development-Nachfolgermodell-ESP8266/dp/B074RGW2VQ/ref=sr_1_3?__mk_de_DE=%C3%85M%C3%85%C5%BD%C3%95%C3%91&keywords=esp32&qid=1565008313&s=gateway&sr=8-3))|Yes
Jumper wires |Female-Female, 0.14 mm²|5||[Amazon](https://www.amazon.de/ZOORE-120pcs-Multicolored-Female-Breadboard/dp/B07P85V1G3/ref=sr_1_5?__mk_de_DE=%C3%85M%C3%85%C5%BD%C3%95%C3%91&keywords=jumper+male&qid=1565690543&s=industrial&sr=1-5)|Yes
Button ||1|2,50 €|[AZ delivery](https://www.az-delivery.de/products/button-modul?_pos=2&_sid=f2080c1b0&_ss=r)|Yes
Power cable for ESP32 - USB-microUSB|Ordinary microUSB phone charger will do|1||[Amazon](https://www.amazon.de/Gritin-Datenkabel-Geflochtene-Robust-Daten%C3%BCbertragung-Grau/dp/B07CJJHVKX/ref=sr_1_3?keywords=usb+c+kabel&qid=1566029225&s=gateway&sr=8-3)|Yes

#### TUT08: Build your first microscope with electronics
Use the parts from TUT06 and TUT07. Above that:

Name | Properties  | Amount|  Price | Link  | Tested
---|---|---|---|---|---
28YBJ-48 Stepper motor with Driver board|DC 5V 4 Phase 5 Wire Stepper Motor With ULN2003 Driver Board|1||[Amazon](https://www.amazon.de/Elegoo-Stepper-Schrittmotor-28BYJ-48-Treiberplatine/dp/B01MEGIHLF/ref=sr_1_1_sspa?__mk_de_DE=%C3%85M%C3%85%C5%BD%C3%95%C3%91&keywords=stepper+arduino&qid=1565008205&s=gateway&sr=8-1-spons&psc=1)|Yes
ESP32 ||1||[Amazon]((https://www.amazon.de/AZDelivery-NodeMCU-Development-Nachfolgermodell-ESP8266/dp/B074RGW2VQ/ref=sr_1_3?__mk_de_DE=%C3%85M%C3%85%C5%BD%C3%95%C3%91&keywords=esp32&qid=1565008313&s=gateway&sr=8-3))|Yes
Jumper wires |Female-Female, 0.14 mm²|10||[Amazon](https://www.amazon.de/ZOORE-120pcs-Multicolored-Female-Breadboard/dp/B07P85V1G3/ref=sr_1_5?__mk_de_DE=%C3%85M%C3%85%C5%BD%C3%95%C3%91&keywords=jumper+male&qid=1565690543&s=industrial&sr=1-5)|Yes
Button ||2||[AZ delivery](https://www.az-delivery.de/products/button-modul?_pos=2&_sid=f2080c1b0&_ss=r)|Yes
Power cable for ESP32 - USB-microUSB|Ordinary microUSB phone charger will do|1||[Amazon](https://www.amazon.de/Gritin-Datenkabel-Geflochtene-Robust-Daten%C3%BCbertragung-Grau/dp/B07CJJHVKX/ref=sr_1_3?keywords=usb+c+kabel&qid=1566029225&s=gateway&sr=8-3)|Yes

We cannot guarantee the availability of the components. If you know other components, please let us know by filing an issue. Thank you :-)

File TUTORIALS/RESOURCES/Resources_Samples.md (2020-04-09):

## Resources: Samples

We cannot guarantee the availability of the components. If you know other components, please let us know by filing an issue. Thank you :-)

### Prepared samples
|  Name | Properties  |  Price | Link  | Tested |
|---|---|---|---|---|
Children Microscope Specimen | 48 pcs, 4 boxes including Animals, Insects, Plants, Flowers | 9€ | [Ebay](https://www.ebay.de/itm/48pcs-Plastik-vorbereitete-Mikroskop-Probe-Kinder-lernen-Wissenschaft-/253139066535) | Yes
Betzold Sample set 2 | 25 pieces | 40€ | [Betzold](https://www.betzold.de/prod/44586/) | Yes
Betzold Sample set 3 | 25 pieces | 45€ | [Betzold](https://www.betzold.de/prod/44587/) | Yes
1ml syringe | for light sheet samples | | [Braun](https://www.bbraun.com/en/products/b/injekt-f-solo.html) | Yes

### Light sheet sample preparation protocol

#### Pollen samples
To prepare agarose gel, 200 mg of standard agarose are dissolved in 10 g of water stirred at room temperature. Afterwards, the temperature is increased to 160 °C. When the solution becomes transparent, the temperature is reduced to 100°C and 0.5 ml of water dissolved pollen is added. After 1 minute of stirring, the solution is collected with a B. Braun 1 ml syringe and submerged in water for cooling down. When the solution solidifies, the tip of the syringe is remove with a scalpel. Finally, the solid solution is partially ejected, therefore the syringe will be used as a sample holder for the microscope.

<p align=center>

<br> Fig.: (a) The syringe is submerged into the agarose embedded pollen (in yellow) and (b) it is
extracted and cooled down into room temperature water until the coagulation. (c) The tip of the
syringe is cut and (d) expelled to be analyzed in the light sheet microscope
</p>

#### Zebra fish samples
The agarose is prepared according to the same protocol as for the pollen samples. The tip of the syringe is cut off, then roughly 0,15 ml of the solution is collected. A single fish is placed on top, sucked in by the syringe and covered with a few drops of agarose. Then again the syringe is submerged in water for cooling down.

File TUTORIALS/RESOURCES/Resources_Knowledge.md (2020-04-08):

## Resources: Link-List

We cannot guarantee the availability of the links. If you know other components, please let us know by filing an issue. Thank you :-)

### Fluorescence
* [DIY Blue Gel Transilluminator](https://openwetware.org/wiki/DIY_Blue_Gel_Transilluminator)
* [DIY Fluorescent Imaging](https://makezine.com/2011/03/04/cheap-diy-gfp-green-fluorescent-protein-illuminator/)
* [DIY Fluorescent Imaging II ](https://dm516.user.srcf.net/?p=107)
* [DIY Fluorescent Imaging III ](http://post.queensu.ca/~chinsang/lab-protocols/gfp-stereoscope.html)
* [GEL Filters for Fluorescent Imaging](http://nic.ucsf.edu/blog/2013/10/theatrical-gels-as-color-filters/)
* [Select the filter for an RPi Microscope](https://github.com/OpenLabTools/Imaging_RPi_Fluorescence/blob/master/content.md)

### Objectives
* [DIY Dipping Objective Lens](http://nic.ucsf.edu/blog/2016/03/converting-an-air-objective-into-a-dipping-objective/)
* [Intro to Eyepieces](http://www.quadibloc.com/science/opt04.htm)
* [DIY Dispersion Staining](https://www.mccroneinstitute.org/uploads/Tricks_DS_Objective-84932.pdf)
* [DIY Phase Contrast](http://www.staff.science.uu.nl/~hooft101/phasecontrast.pdf)

### Mechanics
*  [Open Flexure Stage I](https://2015.igem.org/wiki/images/d/d0/CamJIC-OpenScope-BOM.pdf)
*  [Open Flexure Stage II](https://publiclab.org/notes/mathew/04-17-2016/making-an-openflexure-microscope)
*  [Open Flexure Stage III](https://publiclab.org/notes/mathew/04-17-2016/making-an-openflexure-microscope)
*  [µCube - 3d printed mechanical optics](https://mdelmans.github.io/uCube/)
*  [Bakaros - Fischertechnik goes Optics](https://websites.fraunhofer.de/Bakaros/?page_id=178)

### Optics
* [Koehler Illumination Design](http://www.thepulsar.be/article/building-a-microscope-from-camera-lenses/)
* [Basics of optic design](https://www.edmundoptics.de/resources/application-notes/microscopy/understanding-microscopes-and-objectives/)
* [My Photonics - Lego(R) for optics](http://www.myphotonics.eu/)

### Setups
* [DIY Raman Microscope](http://web.archive.org/web/20150321080612/https://hackaday.io/project/1279/components)

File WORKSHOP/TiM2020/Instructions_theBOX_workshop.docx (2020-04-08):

UC2 workshop

Instructions sheet

Workshop content:

2-4 hours (probably 2 hours), 6-8 participants, three times in the week

1. Short introduction (10 min)
2. The participants can play with the lenses, e.g. try the telescopes (10 min)
3. Build the incubator microscope (with the sketch and all parts are labelled), acquire an image of a test probe: 20 min > experiment 1 (E1)
4. Smartphone microscope: 20 min > experiment 2 (E2)
5. Light sheet microscope: 20 min > experiment 3 (E3)
6. Participants can image their own samples with any of these 3 setups: left time

Notes instructions:

Introductory notes: there are 3 electronic components that are controlled via the Raspberry Pi (RasPi): the LED array, the focusing stage (“Z”) and the sample stage (“X”). They each have their own micro-controller (ESP32) and the command codes should be already uploaded. They are controlled wirelessly by the RasPi but get their power supply through USB (typically, a HUB plugged to the RasPi). Each box contains its own set of components, they are not interchangeable. Therefore, before starting, check that the ID of each component is matching to that of the box. This is also true for the keyboard.

Procedure to set things up before the workshop starts:

1) Plug the router, wait a few minutes
2) Plug the camera in the RasPi BEFORE turning ON

NB: in case a hard reboot of the RasPi is needed, just disconnect the power and plug it in again (no button)

3) Start the RasPi by connecting it to the power socket (password: youseetoo). Insert the dongle of the keyboard
4) The RasPi should connect automatically to the WIFI router, check by clicking on the icon (the name of the WIFI is typically UC2_wifi_some number (password: _lachmannUC2)
5) Open the command window and type python main.py
6) The GUI opens after some time

NB: On the RasPi, one can use either the mouse (integrated in the keyboard) or the display as a touchscreen

7) Check that the camera is working by clicking on “preview”
8) Connect the USB HUB and then power each ESP32 by connecting it to the HUB via USB.

NB: there are typically only 2 micro-USB cables per box because no experiment requires more than 2 of the components at the same time

9) Connect the LED array. It should boot and show the beginning of UC (the C is cut)
10) In the GUI, choose LIGHT, and try the different functions. With CUS (custom), you can choose which LED to turn ON. Check that this is working
11) Connect the Z-stage. Some blue LED should blink on the ESP32
12) In the GUI, choose MOTOR and Z. You can choose the step size in um (16 um minimum, 160 maximum) and then push on the double arrows in one direction or the other. When doing so, some red LED should turn ON on the side of the cube of to the stepper motor (this shows that the command was transferred) + if you observe the screw you should see it moving.

The Z-stage is mostly used for focusing (E1 & E2)

13) To go out of the Z mode, click again on Z
14) Connect the X-stage. Depending on the version, it may be a red LED labelled “ON” which turns on once powered. The principle for moving this motor is the same as for step 12, only under “X”.

NB: the distance in X is not calibrated (but the relations are correct, i.e. a step size “32” will be twice more than a step size “16”! The distance is Z is approximately calibrated correctly.

The X-stage is mostly used for scanning the sample in the light sheet (E3)

There is no absolute zero for the motors, so they will not remember their position before and after boot.

NB: don’t leave the motors ON unnecessarily long (e.g. coffee break) because they get warm

15) GUI > start experiment enables you to acquire a time series (XXX more information missing),
16) GUI>start experiment> custom turns the previously defined custom LED pattern on. Click then on SNAP to acquire a single image frame (saved automatically)

NB: it is necessary to turn on the LED array for acquiring an image, even for the light sheet which actually uses the laser

17) Test building the incubator microscope (E1).

The sketch can be found in UC2-GIT (https://github.com/bionanoimaging/UC2-GIT)/CAD (https://github.com/bionanoimaging/UC2-GIT/tree/master/CAD)/APP_Incubator_Microscope (https://github.com/bionanoimaging/UC2-GIT/tree/master/CAD/APP_Incubator_Microscope)/IMAGES (https://github.com/bionanoimaging/UC2-GIT/tree/master/CAD/APP_Incubator_Microscope/IMAGES)/UC2_fullBOX_incubator_EN.pdf

18) Good samples for the incubator microscope: pretty much all of the Betzold boxes. The fly head is a good sample for showing what happens when you replace the 10x objective with a 4x objective (bigger FOV)
19) Test building the smartphone microscope (E2)
20) XXX (here comes more about the smartphone microscope)

NB: there are not as many phones as boxes, so some participants will have to use their own phone. The phone will only be used for its camera and not as a controller through the app

21) Put up the light sheet experiment (E3): insert the laser pointer in its cube, turn it on using the clamp, check alignment/align with hex key. Then comes the cube with the beam expander and collimator: check that the beam is approximately collimated. This consists of a smartphone lens and a 25 mm focal length lens. The smartphone lens can be slightly moved back and forth for collimation. Then comes the cylindrical lens which typically is at the very end of its cube. The objective lens is taken out of the 4x objective (which contains actually only 1 lens). The detection unit (two cubes objective + motor) has to be slightly modified for E3 with respect to E1 and E2: carefully remove the objective and put it back in the other way around

XXX Sketches and/or pictures of the optimal position of the objective in its holder will be inserted here!

NB: if one turns the cylindrical lens of 90°, it is possible to observe the light sheet in the FOV of the camera and for example measure its thickness

NB: the light sheet experiment is more sensitive to stray light than others

22) Sketch for the light sheet can be found under UC2-GIT (https://github.com/bionanoimaging/UC2-GIT)/CAD (https://github.com/bionanoimaging/UC2-GIT/tree/master/CAD)/APP_LIGHTSHEET_Workshop (https://github.com/bionanoimaging/UC2-GIT/tree/master/CAD/APP_LIGHTSHEET_Workshop)/IMAGES (https://github.com/bionanoimaging/UC2-GIT/tree/master/CAD/APP_LIGHTSHEET_Workshop/IMAGES)/UC2_fullBOX_lightsheet_EN.pdf
23) Alignment of the light sheet setup:
- The laser has a line which should be consistent to the direction of the light sheet i.e. vertical
- Check that the laser spot is collimated (its size doesn’t change): if needed, move the smartphone lens
- Check that the last spot is homogeneous: use the 4 screws that hold the laser in place. They should be in contact with the plastic mount, not directly on the laser pointer
- The cylindrical lens typically should be as far as possible in its cube. The flat side is towards the mirror, and as close as possible to the mirror
- The 4x objective (illumination objective) typically should be as far as possible in its cube. For its orientation, imagine the mounting (which was removed) of the objective: the threading is towards the mirror, the front lens towards the sample
- Adjust the kinematic mirror so that light goes through the illu. objective nicely
- Typically it may be at this point that the produced light sheet is too low and everything has to be raised up (the laser pointer, the collimator, and the illu objective can be slightly lifted up)
- Releasing the screws on the cube of the illu objective of 2 turns also will lift the objective slightly up
- Now we must align the detection part. For this we use the alignment sample made of lens cleaning tissue with a marker pen inside of the special holder
- put the flash light behind the sample with the camera ON
- Move the sample by hand until you focus on some fibres. Try to bring the focus in the middle of the field of view
- Make sure the sample is approximately at the centre of its cube (on the x-stage)

Important: the laser pointer is strong! If it is turned on while there is no sample, this is a real laser hazard!

24) For looking at acquired images: close the GUI, click on the file manager icon, go to UC2/RASPIapp-py3/data where there will be a new folder which name is a date (this date might be wrong, just choose the newest date). Inside of this folder, there is a first empty sub-folder. All saved images are in the next one (in .jpg format and with an automatic name).

Important: if the GUI crashes, after restart the new images will be named with the same convention starting from 1 again and therefore will overwrite images saved before the crash. Therefore, in case of a crash, rename or move your images!

25) Shut down procedure: Raspberry symbol > shut down

For a box where the phone is the master (e.g. Aurélie’s box):

Follow the instructions 1-5.

6) in the terminal, write raspistill -k ENTER: this opens the screen

7) turn on the phone. Activate the hotspot (UC2_wifi01)

8) open the UC2 controller app and press GO: it should connect

9) Connect the LED and the motors to the USB hub: all should be recognized (the camera gets connected as step 1)

10) raspistill -o ImageName saves an image under Desktop/ImageName.jpg

11) raspivid -o saves a video under Desktop/VideoName.h204

NB: It is possible to change the format to mp4, see Eda’s email

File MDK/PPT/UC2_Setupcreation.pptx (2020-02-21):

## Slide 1

Toolbox of available UC2-Parts

Dichroic

Tholabs

Kinematic
Mirror

Cellphone

Z-stage

LED

Laser Holder

BS

S-stage

Mirror

Sample Holder

Sample Holder - comb

Lens

Eyepiece

CAM

Beamexp.

Kinematic
Mirror

LED
Array

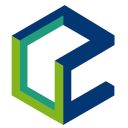
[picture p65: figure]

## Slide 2

Playground for
optical setups

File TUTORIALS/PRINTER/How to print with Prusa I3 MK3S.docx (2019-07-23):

# How to print UC2 with Prusa I3 MK3S:

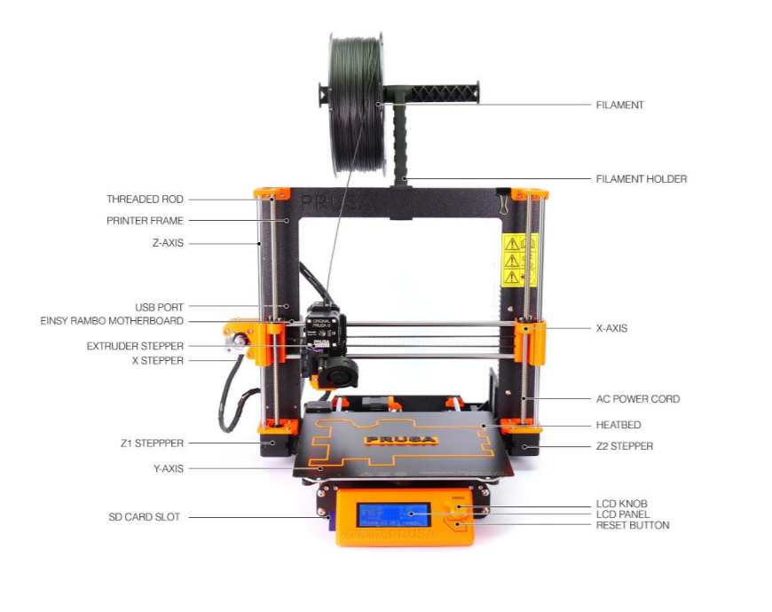
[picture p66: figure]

## Setup Cura for the Prusa i3

- Download Cura settings from https://www.prusa3d.com/drivers/ and install according to instructions
- Go to: https://manual.prusa3d.com/Guide/How+to+import+profiles+to+Cura/1421#_ga=2.216762066.53635997.1563870317-1002203748.1563870317
- Download the archive and unpack it somewhere
- Go to Cura and import the different .curapfile files one by one -> Cura_OriginalPrusa_Profiles\Cura_3_6_0\mk3_cura_profiles\MK3_cura_profiles\04_Cura_layerheight_profiles

# Settings for UC2 prints

- For printing UC2 parts use profile MK3S_MK3_0,15_Optimal.
- Change infill to 50%.
- In general no support is necessary (especially for all bas-cubes and the Z-stage!)
- Material: Prusa Research Prusament PLA.
- Safe gcode to SD card.

# Printing the parts with the Prusa

- Switch on the printer (on the back, right side).
- Clean the steel sheet (build plate) with isopropylalcohol and tissue.
- Insert SD card.
- Push the control knob next to the screen (if SD card does not open automatically).
- Choose Print from SD.
- Choose your file.
- Watch the first layer or two to see if they attach properly.
- In case something goes wrong, press the reset button (X).
- Wait till your print is finished.
- Wait for it to cool down to room temperature. You can see the heatbed temperature on the screen.
- Remove the steel sheet.
- Bend the steel sheet so the parts separate from it.

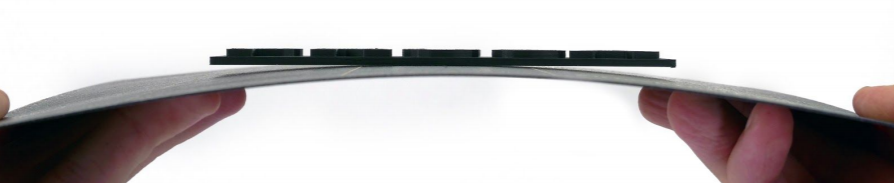
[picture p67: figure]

- Return the steel sheet to its correct position.

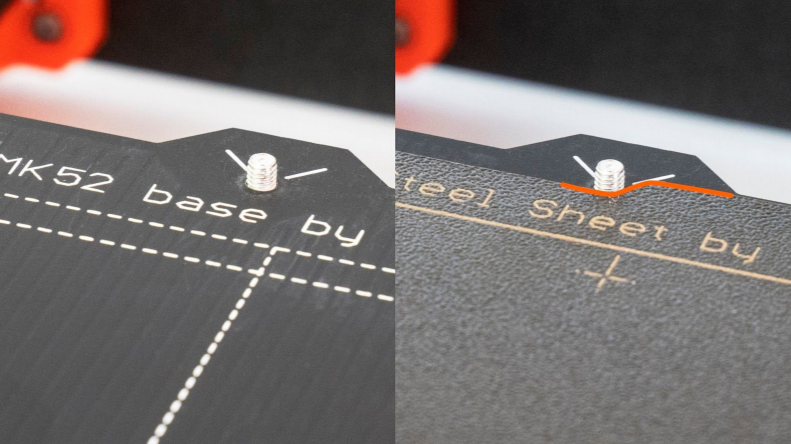
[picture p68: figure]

For more information – Printing Handbook https://cdn.prusa3d.com/downloads/manual/prusa3d_manual_mk3s_en_3_11.pdf#_ga=2.211631766.2016905863.1563777341-710825333.1558506269

We print with PLA 1,75 mm!

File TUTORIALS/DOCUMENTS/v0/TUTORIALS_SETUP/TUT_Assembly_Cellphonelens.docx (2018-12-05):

# Use a cellphone Lens As a Microscope

Get an old cellphone Camera and use it as a simple microscope.

The basic concept is to negate the refractive power of the objective lens of a cellphone camera by mounting a 2nd lens from an old cellphone camera inversely in front of the camera. This produces a -1:1 imaging system with a large field of view and a very low price.

Benedict Diederich

V0; 05.12.18

# Table of Content

# Motivation

- Build a cheap cellphone microscope.
- How is it working
- What do we need to accomplish that?

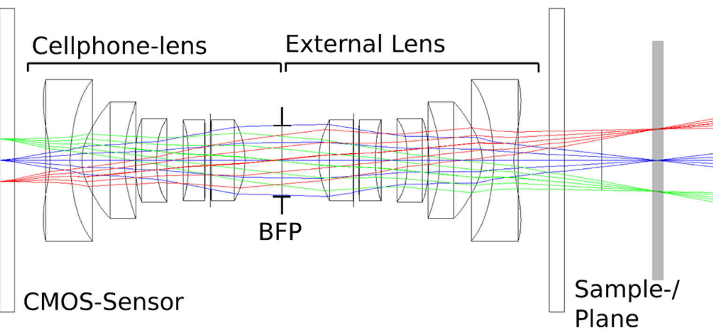
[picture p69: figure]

Goals
At the end you should have learned the following:

- Get the lens
- Mount it on the cellphone camera
- Image stuff
- Understand the imaging theory

# Bill of Materials

Quantity | Description/Name | Image | Price

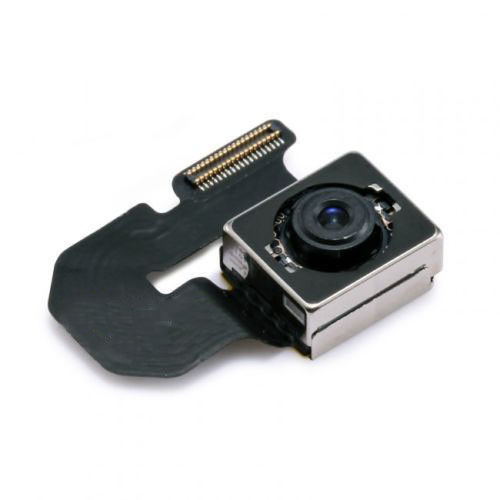
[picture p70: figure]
Fuer-iPhone-6-Plus-HauptKamera-Rueckkamera-Rear-Back-Camera-Module-Flex-Original

1 | iPhone 6 camera module - 1/2.4 f#, very cheap - https://www.ebay.de/itm/Fur-iPhone-6-Plus-HauptKamera-Ruckkamera-Rear-Back-Camera-Module-Flex-Original/153155444315?hash=item23a8c69e5b:g:q6UAAOSwQf9be44Z:rk:1:pf:0 | | 5-12€

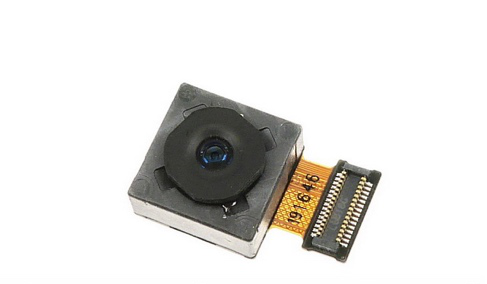
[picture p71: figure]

2 | LG G6 H870 Medium Rückseite Kamera Modul - 1/2.4 f#, X/Y/Z voice-coil actuator - https://www.ebay.de/itm/LG-G6-H870-medium-back-side-camera-flex-cable-module-contact/391883007082?epid=2231365189&hash=item5b3e0c246a:g:bjoAAOSwiqdaoeUs:rk:3:pf:0 | | 15€

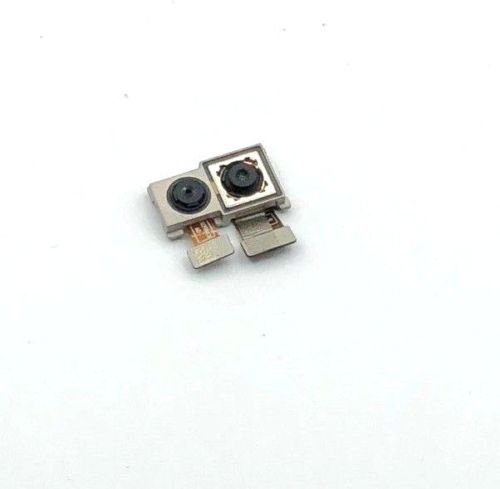
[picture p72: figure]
Original-Huawei-P20-Lite-Haupt-Kamera-Hintere-Camera-Flex-Hauptkamera-Back

1 | Huawei P20 Camera Lite - 1/1.6 f# - https://www.ebay.de/itm/Fur-Huawei-P20-Lite-Reparatur-Back-Kamera-Cam-Flex-Ersatzteil-Hauptkamera-Camera/362329660012?hash=item545c87da6c:g:96kAAOSwTFhbBqtt:rk:23:pf:0 | | 16€

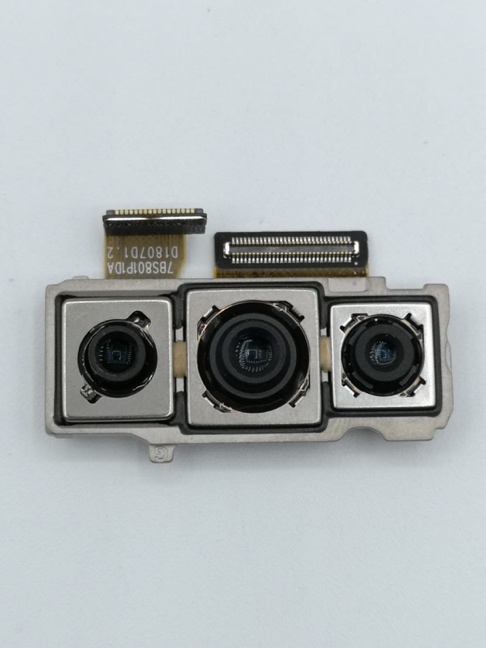
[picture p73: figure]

1 | Huawei P20 Pro - https://www.ebay.de/itm/Original-Huawei-P20-Pro-Haupt-Kamera-Flex-Hinten-Ruck-Foto-Main-Camera-Back-Rear/273577104409?hash=item3fb2775419:g:Rt8AAOSwIw1b-TC6:rk:26:pf:0 | | 60€

# Step by Step guide for extracting the lens (LG G5)

Attention: Take care of your fingers! Don’t cut yourself!

## 1st Step – Prepare everything

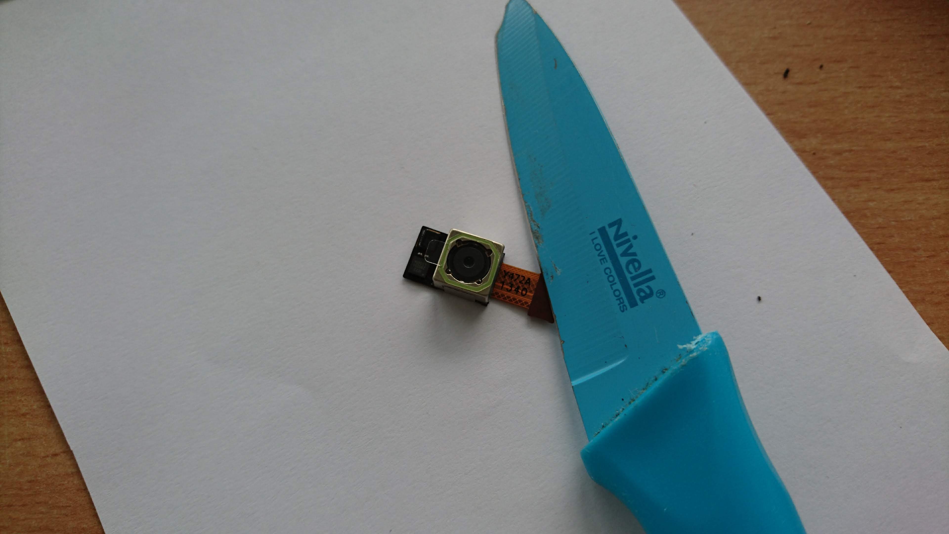
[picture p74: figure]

## 1st Step – separate soldered lens from Sensor PCB

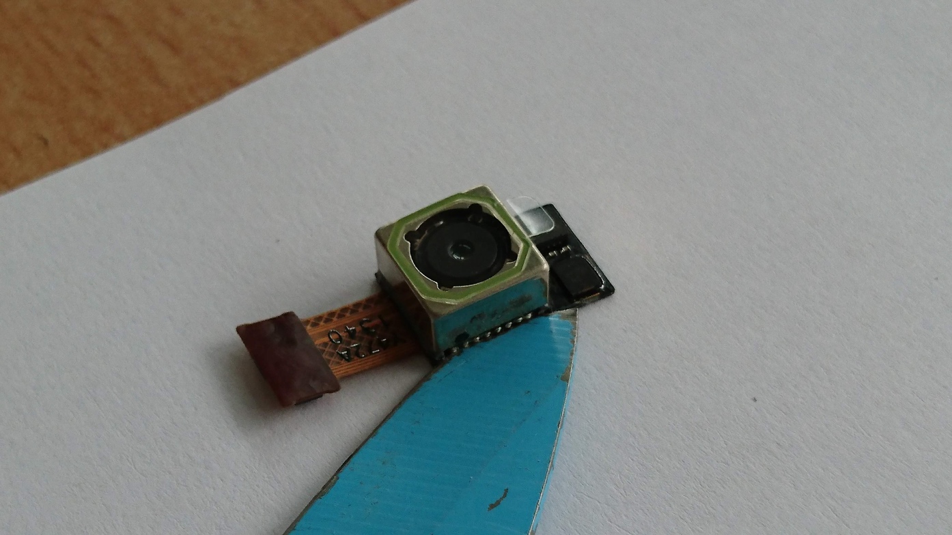
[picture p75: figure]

You could melt the soldering, but a sharp knife will do the same job.

## 3rd Step – separate Sensor and lens

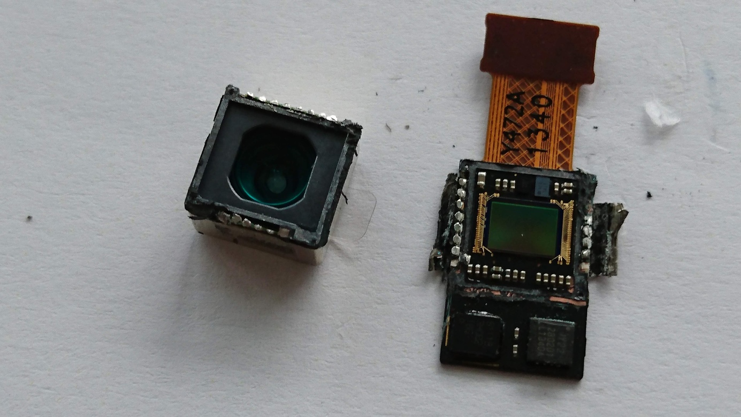
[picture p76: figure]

## 4th Step – Remove IR Filter (Optional)

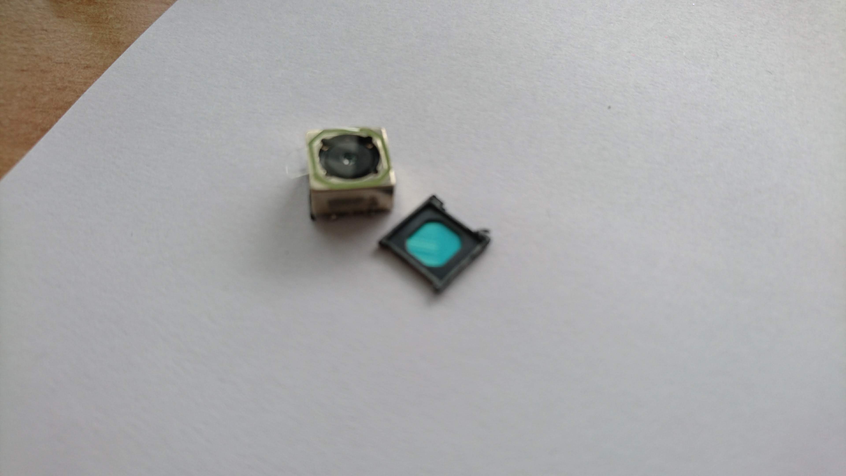
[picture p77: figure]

## 5th Step – Solder lens on PCB for controling XYZ-movement (Optional)

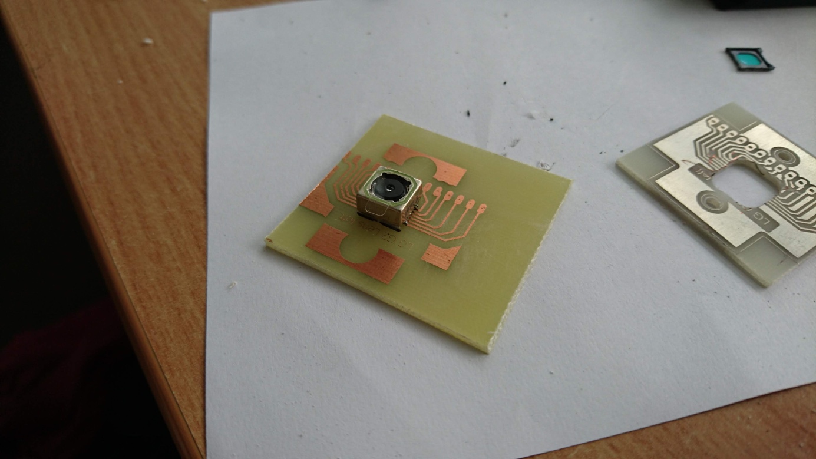
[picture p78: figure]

## 6th Step – Testing

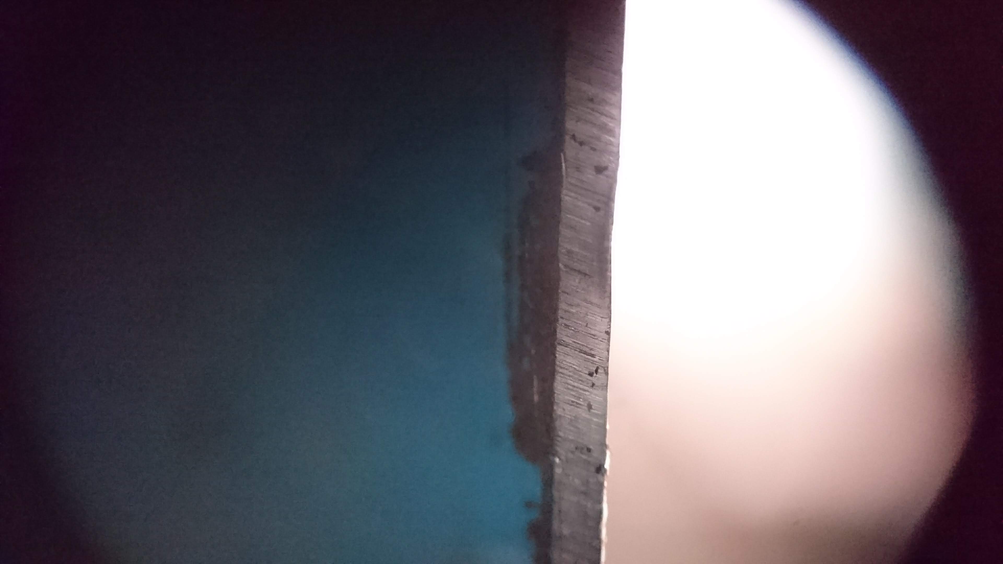
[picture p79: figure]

You can simply take some blutek or douple-sided sticky tape to mount the lens directly in front of the cellphone camera. The image above is the blade of the knife we used above. The better the entrance pupil of the cellphone matches the exit pupil of the cellphone lens, the better the image gets.

# Theoretical

The lens assures a -1:1 imaging system and is almost free of any aberation up to an NA of 1/(2*f#)=0.315 in Case of the Huawei P20. The field of view – depending on which camera is used – can be up to 12x7mm^2.

More theoretical aspects are coming soon!

# Useful links and Resources

## Links

- Cellphone Microscope relying on setup above:
  - https://journals.plos.org/plosone/article?id=10.1371/journal.pone.0192937
- Cellphone Microscope where idea originally came from:
  - https://www.ncbi.nlm.nih.gov/pmc/articles/PMC4031072/
- FPM Setup where they used cellphone lenses:
  - https://www.ncbi.nlm.nih.gov/pmc/articles/PMC4206303/

1 - You See Too

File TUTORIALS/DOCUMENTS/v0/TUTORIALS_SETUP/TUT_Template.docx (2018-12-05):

# TITLE of the setup

Short introduction of what to expect from the setup goes here.

Lorem ipsum dolor sit amet, consetetur sadipscing elitr, sed diam nonumy eirmod tempor invidunt ut labore et dolore magna aliquyam erat, sed diam voluptua. At vero eos et accusam et justo duo dolores et ea rebum. Stet clita kasd gubergren, no sea takimata sanctus est Lorem ipsum dolor sit amet. Lorem ipsum dolor sit amet, consetetur sadipscing elitr, sed diam nonumy eirmod tempor invidunt ut labore et dolore magna aliquyam erat, sed diam voluptua. At vero eos et accusam et justo duo dolores et ea rebum. Stet clita kasd gubergren, no sea takimata sanctus est Lorem ipsum dolor sit amet.

Author 1

Author 2

V0; Date

## Table of Content

## Motivation

- Why we want to do it?
- What’s the major goal?
- Where can you find this?

Fancy Image can go here! (SRC)

Goals
At the end you should have learned the following:

- What is light?
- What is diffraction?
- 3D printing with UC2
- Etc.

Outline

Coarse Overview of necessary steps

1. Get the Parts ready
  a. Download
  b. 3D print
  c. Assembly
2. Build a *XXX
3. Do Experiment 1
4. Do Experiment 2
5. Conclusion

# Prepare the *XXX Setup (Practical Part)

Here we want to show the basic system description and how the different parts interact with each other.

## Full Setup

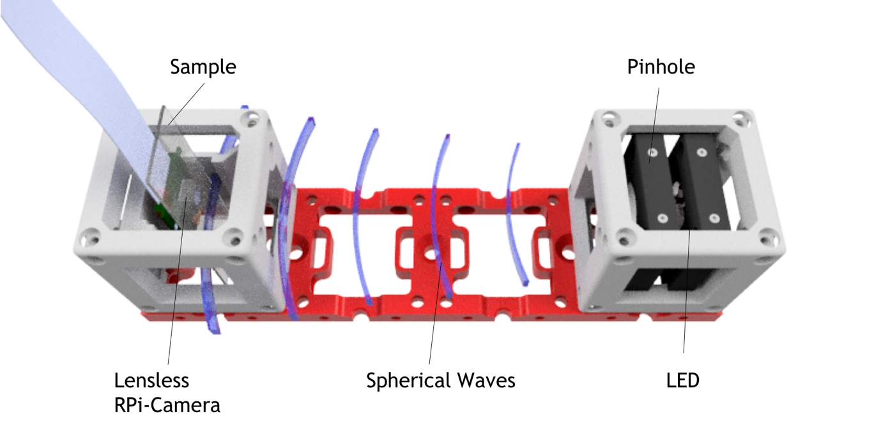
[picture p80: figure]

Figure 1 – This is how it should look like once it’s ready.

## Bill of Materials

Quantity | Description/Name | Image | Price

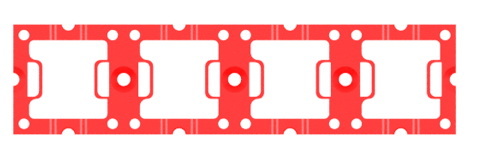
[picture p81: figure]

1 | Grundplatte (1x4) - https://github.com/bionanoimaging/UC2-GIT/blob/master/CAD/INLINE_HOLOGRAM/STL/INLINE_HOLOGRAM_00_Base_4x1_v0.stl | | 1€

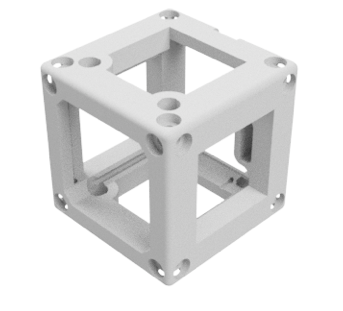
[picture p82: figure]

2 | Cube (2x), 2 Teile - https://github.com/bionanoimaging/UC2-GIT/blob/master/CAD/INLINE_HOLOGRAM/STL/INLINE_HOLOGRAM_10_Cube_v0.stl - https://github.com/bionanoimaging/UC2-GIT/blob/master/CAD/INLINE_HOLOGRAM/STL/INLINE_HOLOGRAM_10_Lid_el_v0.stl | | 1€

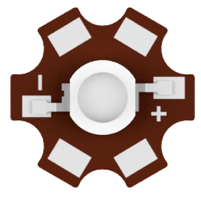
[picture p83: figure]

1 | LED (Royal blue, i.e. 1W-3W, Star PCB attached) - https://www.amazon.com/Led-World-Extreme-Royal-445-450nm/dp/B00MNB4LJU | | 2€

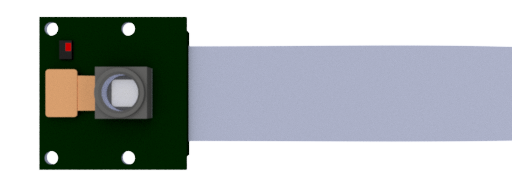
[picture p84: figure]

1 | RPi Camera v2 - https://shop.pimoroni.de/products/raspberry-pi-camera-module-v2-1-with-mount Alternative für Pi Zero: - https://shop.pimoroni.de/products/raspberry-pi-zero-camera-module | | 15€-33€

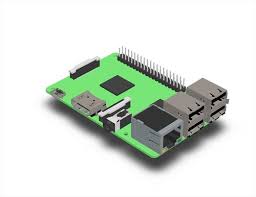
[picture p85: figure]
/var/folders/4w/k4yhf14j7xsbp2jd85yk555r0000gn/T/com.microsoft.Word/Content.MSO/45DC5D6D.tmp

1 | Raspberry Pi V3 + 1SD Micro Card (prebuilt binaries) - https://shop.pimoroni.de/products/raspberry-pi-3-b-plus Alternativ: 1x Raspberry Pi Zero + 1SD Micro Card (8GB) - https://shop.pimoroni.de/products/raspberry-pi-zero-w | | 45€ / 15 €

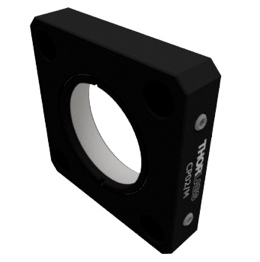
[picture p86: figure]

2 | Thorlabs CP02 - https://www.thorlabs.com/thorproduct.cfm?partnumber=CP02 Alternative: Selber drucken | | 20€
1 | Netzteil, 5V USB, Raspberry - https://www.reichelt.de/usb-ladegeraet-5-v-2500-ma-micro-usb-nt-musb-25-sw-p167078.html?PROVID=2788&gclid=Cj0KCQjw3ebdBRC1ARIsAD8U0V5RBH3hKsPJiLh7Pk8SBP6UYqJqPXgTA_QfsG1lmuD5Y75ie5qSEMIaAiNCEALw_wcB&&r=1 | | 5€
| Zusätzliches Material, was ggf. bereits verfügbar ist. - Alufolie - Alumnium Sheet ca. 30x30 mm, rund? (dickere Aluminium Folie) - Dünne Nadel - Klebestreifen - USB-Stick - Tastatur/Maus | | 10€
16 | Kugelmagneten NeoDym, D=6mm - https://www.ebay.de/itm/50x-POWER-NEODYM-KUGEL-MAGNET-6-mm-N35-EXPERIMENT-BASTEL-TAFEL/201693302926?hash=item2ef5db908e:g:QgUAAOSwpLNYBJt7 | | 10€
16 | Schrauben (DIN 912, M3, 18mm, kein Edelstahl! Müssen magnetisch sein-> Eisen!) - https://www.conrad.de/de/toolcraft-839670-zylinderschrauben-m3-12-mm-innensechskant-din-912-iso-4762-stahl-88-geschwaerzt-100-st-839670.html | | 1€
4 | Alu-Stangen (50mmxD6mm) - https://www.ebay.de/itm/7960-Alu-Aluminium-Rundstab-6-12mm/321920077077?hash=item4af3ee8d15:m:m6S16XrMjjoQHAna_7z12Ug | | 4 €
1 | 100R Widerstand, 1W, oder 4x 400R 0.25W parallel | | 1 €
1 | (USB) Kabel (defektes Gerät, Schrott), ca. 40cm | | 1 €
1 | Proben: Duschgel mit Glitzereffekt, Mikrokugeln, Epithelzellen
1 | Probenpräparationskit, Pipette, Deckgläschen, Objektträger (120x70mm) https://www.msg-praxisbedarf.de/MENZEL-Objekttraeger-MIT-Mattrand-50-Stueck.htm?websale8=msg&pi=58150&ref=froogle&subref=MEG101126M&gclid=Cj0KCQjw3ebdBRC1ARIsAD8U0V5Luk5NOQ_5EgCx-r_ZP_9B5Slwe-cPsXAOKK-Mx73bsF8DHiD24gEaArfkEALw_wcB | | 5€

Assembly

Quick explained Photo-Story to show how the parts belong together.

Lorem ipsum dolor sit amet, consetetur sadipscing elitr, sed diam nonumy eirmod tempor invidunt ut labore et dolore magna aliquyam erat, sed diam voluptua. At vero eos et accusam et justo duo dolores et ea rebum. Stet clita kasd gubergren, no sea takimata sanctus est Lorem ipsum dolor sit amet. Lorem ipsum dolor sit amet, consetetur sadipscing elitr, sed diam nonumy eirmod tempor invidunt ut labore et dolore magna aliquyam erat, sed diam voluptua. At vero eos et accusam et justo duo dolores et ea rebum. Stet clita kasd gubergren, no sea takimata sanctus est Lorem ipsum dolor sit amet.

Software Used in this Tutorial (Optional)

- Fiji (https://imagej.net/Fiji/Downloads)
- Anaconda Python (3.6) ( https://www.anaconda.com/download)
- Cura (https://ultimaker.com/en/products/ultimaker-cura-software)
- Tinkercad.com

## Prepare Software to make Software work (Optional)

- Download Pi-Image
- Flash Pi-Image
- Connect Pi to Wifi

# Theoretical Part for the *XXX

Introduction

Lorem ipsum dolor sit amet, consetetur sadipscing elitr, sed diam nonumy eirmod tempor invidunt ut labore et dolore magna aliquyam erat, sed diam voluptua. At vero eos et accusam et justo duo dolores et ea rebum. Stet clita kasd gubergren, no sea takimata sanctus est Lorem ipsum dolor sit amet. Lorem ipsum dolor sit amet, consetetur sadipscing elitr, sed diam nonumy eirmod tempor invidunt ut labore et dolore magna aliquyam erat, sed diam voluptua. At vero eos et accusam et justo duo dolores et ea rebum. Stet clita kasd gubergren, no sea takimata sanctus est Lorem ipsum dolor sit amet.

Formulas

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

A=c*x+b

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

Etc.

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

# Experiments

Experiment 1

What to do?

What do you observe?

What do you expect?

Why?

Experiment 2

# Conlcusion

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

# Usefull links and Ressources

## Ressources

## Links

- https://www.jpl.nasa.gov/edu/learn/project/how-to-make-a-pinhole-camera/
- http://pinholemoustache.com/wp-content/uploads/2015/09/2c-cu-acul-cu-grija-stenopa.jpg

1 - You See Too

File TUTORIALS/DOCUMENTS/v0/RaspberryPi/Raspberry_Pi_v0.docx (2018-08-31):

# Setup for the Raspberry Pi Control Interface

V0, 24.08.2018

X. Uwurukundo

B. Diederich

# Introduction

The control interface is a Raspberry Pi 3, connected to the 7 inch touchscreen baked into a 3D printed case. It acts as the acquisition synchronization interface, controlling the I2C hardware, the camera and manages the memory/connections.

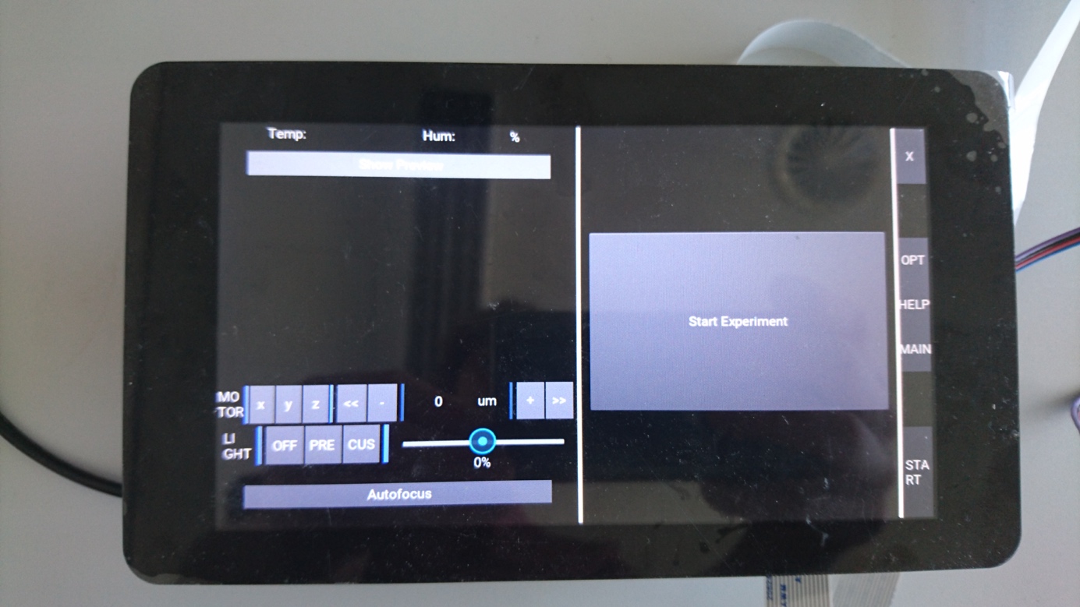
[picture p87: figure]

# Components / Resources

Below you’ll find a list with the basic ingredients for the control interface to work

Article | Image | Price/Link

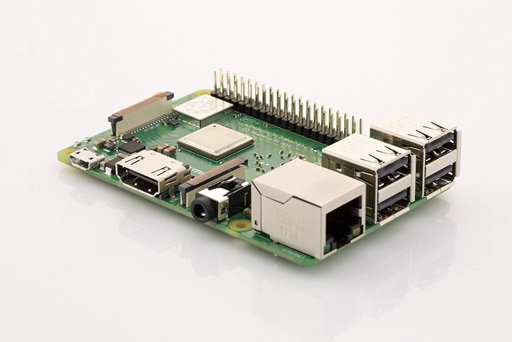
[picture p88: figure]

Raspberry Pi 3 | | 35 €, https://www.amazon.de/Raspberry-1373331-Pi-Modell-Mainboard/dp/B07BDR5PDW/ref=sr_1_1?ie=UTF8&qid=1534931804&sr=8-1&keywords=Raspberry+Pi

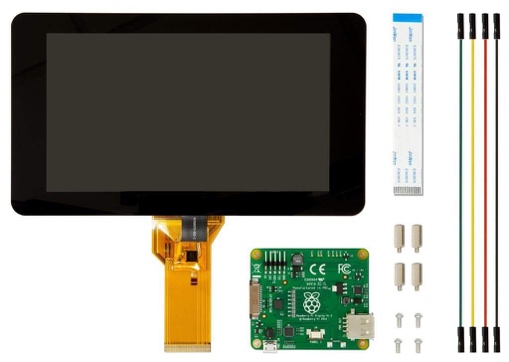
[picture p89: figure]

7 inch touchscreen | | 70 €, https://www.amazon.de/Raspberry-Pi-7-inch-Screen-Display/dp/B014WKCFR4/ref=sr_1_3?ie=UTF8&qid=1534934546&sr=8-3&keywords=Raspberry+Pi+7+inch
SD Card, 64 GB | | 10 €

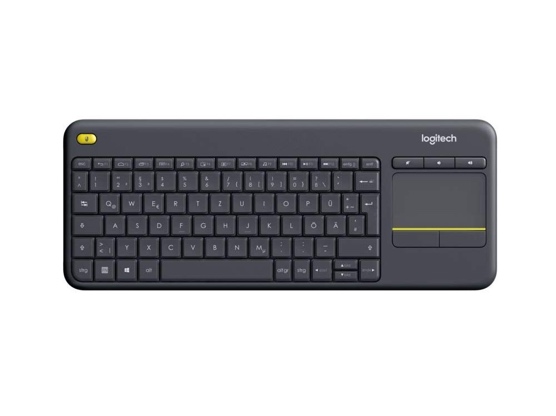
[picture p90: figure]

Logitech Keyboard + Trackpad | | 35€, https://www.amazon.de/Logitech-Wireless-Tastatur-Deutsches-Tastaturlayout/dp/B00VHHWNMI/ref=sr_1_3?ie=UTF8&qid=1534934623&sr=8-3&keywords=logitech+tastatur+touch
Pi Camera v 2.1 | | 15€
Ribbon Cable 1m | | 3€

# Assembly

It is recommended to buy/print a case for the Raspberry Pi and the 7 inch touchscreen. We made good experiences with the original Pi-Screen though it’S more expensive. It ships with all necessary parts (screws, mounting material). For an assembly guide please have a look here:

https://thepihut.com/blogs/raspberry-pi-tutorials/45295044-raspberry-pi-7-touch-screen-assembly-guide

For the I2C connection use the pins below (SDA/SCL):

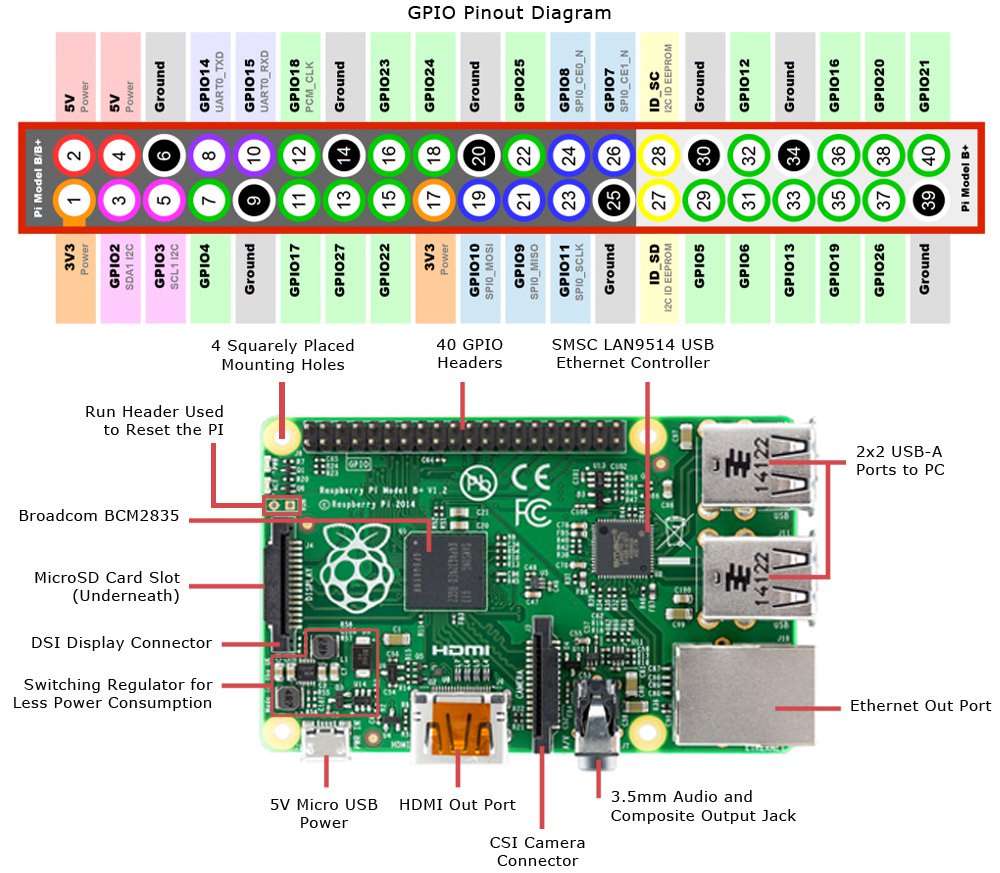
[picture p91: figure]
Bildergebnis fÃ¼r Raspberry Pi pinout

5V, Gnd also connects to the external components. The 5V power supply can either be used through the USB-connector or the 5V input of the Pi (take care it’s not fused!).

# Soldering/Wiring/Camera connection

# Install Stuff on Arduinos (I2C-Devices)

Right now there are several examples to run with the U2C toolbox:

- Light-Source
- XYZ-Stage
- Z-Stage
- XY-Stage
- LED Matrix

All of them are backed with an Arduino acting as the “communicator”. It states the set of available functions with a hand-shake protocol at the beginning and makes sure that the requested commands over I2C coming from the master (Raspi) are executed. Each Device needs a specifc Address which has to be set in the Arduino files (Arduino folder).

You can implement what-ever device you want. For further information please have a look in the I2C guide.

To install the Arduino stuff, please download the Arduino IDE and flash the .ino files to you Nano’s.

# Install OS

Download stable Raspbian Version and flash it on the SD-Card.

# How-to setup the Raspberry Pi

Step-by-Step Guide to Set-up Raspbian Stretch

Disclaimer: Note that the Raspberry Pi Zero – although running Raspbian Stretch as all other Raspberry Pi’s – is ARMv6 architecture in contrast to the most common ARMv7 architecture as used on the Raspberry Pi 3. However, all steps described in this guide should work on both and were tested on a Raspberry Pi Zero W.

Before you begin, check your default python version with:

- pi@raspberrypi:~$ python --version

This guide is written for python 2.7 and assumes it is the default python-compiler on the target system. All steps were performed under afore-mentioned conditions and systems only. Apart from this, it is highly recommended that all pip-installs are run as follows:

- Instead of: pi@raspberrypi:~$ ~~pip install numpy~~
- Better run: pi@raspberrypi:~$ python -m pip install numpy

This will install the package more specific to your default-compiler and showed advantages relating dependencies-setup.

1) Browse to: https://www.raspberrypi.org/downloads/raspbian/
2) Download Raspbian Stretch
3) Flash it to Micro-SD-Card with at least 8GB capacity (e.g. with Etcher on Windows)
4) Set up your WiFi-Connection if not already done
5) Optional: First get packagelist with package size and then get rid of unnecessary packages in order to free some space on your SD-Card:
- pi@raspberrypi:~$ dpkg-query -Wf '${Installed-Size}\t${Package}\n' | sort -n
- pi@raspberrypi:~$ sudo apt-get remove --purge wolfram-engine
- pi@raspberrypi:~$ sudo apt-get clean
- pi@raspberrypi:~$ sudo apt-get autoremove
6) Install Kivy for Raspbian Stretch ( according to https://kivy.org/docs/installation/installation-rpi.html ):
- pi@raspberrypi:~$ sudo apt-get update
- pi@raspberrypi:~$ sudo apt-get install libsdl2-dev libsdl2-image-dev libsdl2-mixer-dev
- pi@raspberrypi:~$ sudo apt-get install libsdl2-ttf-dev pkg-config libgl1-mesa-dev
- pi@raspberrypi:~$ sudo apt-get install libgles2-mesa-dev python-setuptools libgstreamer1.0-dev
- pi@raspberrypi:~$ sudo apt-get install git-core gstreamer1.0-plugins-{bad,base,good,ugly}
- pi@raspberrypi:~$ sudo apt-get install gstreamer1.0-{omx,alsa} python-dev libmtdev-dev
- pi@raspberrypi:~$ sudo apt-get install xclip xsel
- Install Kivy globally on your system but with the following command
7) Install Cython 0.28.3 ( according to https://kivy.org/docs/installation/installation-rpi.html ):
- pi@raspberrypi:~$ sudo python -m pip install -U Cython==0.28.3 (takes approx. 2h on RasPi Zero)
8) Install Kivy ( according to https://kivy.org/docs/installation/installation-rpi.html ):
- pi@raspberrypi:~$: sudo pip install git+https://github.com/kivy/kivy.git@master

(takes approx. 2h on RasPi Zero)

9) Open RasPi Config and activate SSH:
- pi@raspberrypi:~$ sudo raspi-config
- Navigate to: Interfacing Options SSH Enable SSH Yes
10) Connect to your Raspberry Pi using its IP-Address within your Network (e.g. with PuTTy on Windows
11) Create Folder “Programming” in home directory. Change into that folder via SSH-Terminal
12) Fetch FludiscopeApp from Benedict Diederichs Branch on GitLab:
- pi@raspberrypi:~$ git clone -b developBD --single-branch git@gitlab.com:renerichter/PPS-app.git
13) Browse to: ~/Programming/PPS-app/code/
14) Run: python main.py
15) Install all missing dependencies you are notified about to be missing (list may be incomplete):
- pi@raspberrypi:~$: python -m pip install unipath
- pi@raspberrypi:~$: python -m pip install ruamel.yaml
- pi@raspberrypi:~$: sudo apt-get install libffi-dev
- pi@raspberrypi:~$: python -m pip install cffi
- pi@raspberrypi:~$: python -m pip install smbus-cffi
- pi@raspberrypi:~$: python -m pip install pyusb
- pi@raspberrypi:~$: python -m pip install safe-cast
16) Install pre-compiled OpenCV 2.4.9.1 as described in order to save hours of compile-time as opposed to widespread conventional install. Get OpenCV-dependencies in advance. And check it installed correctly afterwards.
- pi@raspberrypi:~$: sudo apt-get update
- pi@raspberrypi:~$: sudo apt-get upgrade
- pi@raspberrypi:~$ sudo apt-get install libtiff5-dev libjasper-dev libpng12-dev
- pi@raspberrypi:~$ sudo apt-get install libjpeg-dev
- pi@raspberrypi:~$ sudo apt-get install libavcodec-dev libavformat-dev libswscale-dev libv4l-dev
- pi@raspberrypi:~$ sudo apt-get install libgtk2.0-dev
- pi@raspberrypi:~$ sudo apt-get install libatlas-base-dev gfortran
- pi@raspberrypi:~$ sudo apt-get install libopencv-dev python-opencv python-picamera
- pi@raspberrypi:~$ python
- >>> cv2.__version__
17) Enable I2C, Serial Communication and PiCamera:
- pi@raspberrypi:~$: sudo raspi-config
18) Optional [RasPi 3]: Install TeamViewer for remote maintenance:
- pi@raspberrypi:~$: sudo apt-get update && sudo apt-get dist-upgrade
- pi@raspberrypi:~$: wget http://download.teamviewer.com/download/linux/version_11x/teamviewer-host_armhf.deb
- pi@raspberrypi:~$: sudo dpkg -i teamviewer-host_armhf.deb (will throw some errors, that’s okay)
- pi@raspberrypi:~$: sudo apt-get -f install (will fix previous errors)
19) Optional [RasPi Zero W]: Install TeamViewer for remote maintenance:
  - pi@raspberrypi:~$: sudo nano /etc/dphys-swapfile
20) Install UC2 Software
  - Git clone XXX –recursive
21) Start Software
  - python main.py

# Software download

For the future we want to release a ready-to-download image for the pi. Please be patient

# Troubleshooting

Intentionally left blank.

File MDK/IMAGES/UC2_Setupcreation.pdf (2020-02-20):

Tholabs

Mirror

Dichroic

Kinematic
Mirror

CAM

Sample Holder

Beamexp.

BS

Lens

Laser Holder

Eyepiece

Z-stage

S-stage | Sample Holder - comb

LED

LED
Array

Kinematic
Mirror

Cellphone

# Toolbox of available UC2-Parts

# Playground for optical setups

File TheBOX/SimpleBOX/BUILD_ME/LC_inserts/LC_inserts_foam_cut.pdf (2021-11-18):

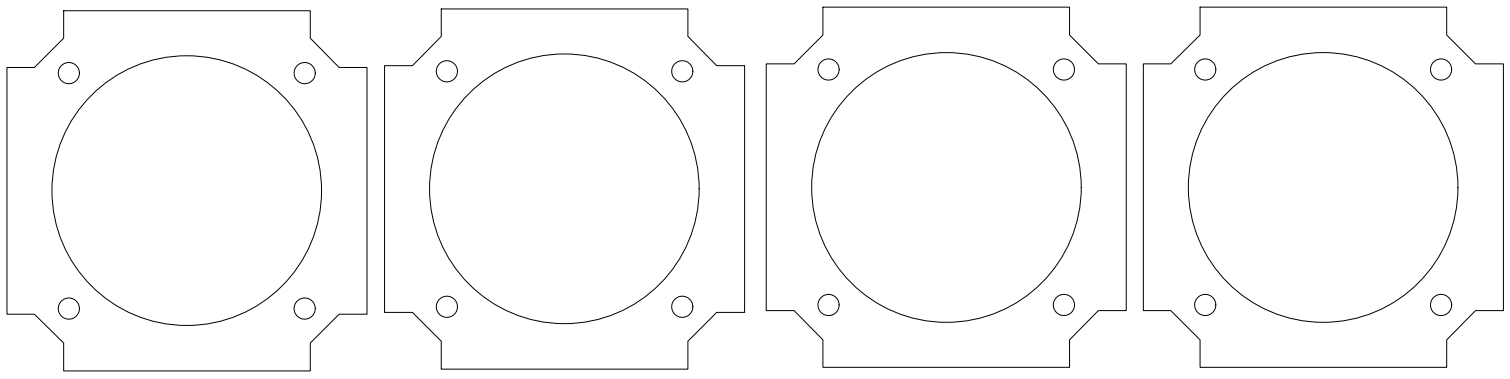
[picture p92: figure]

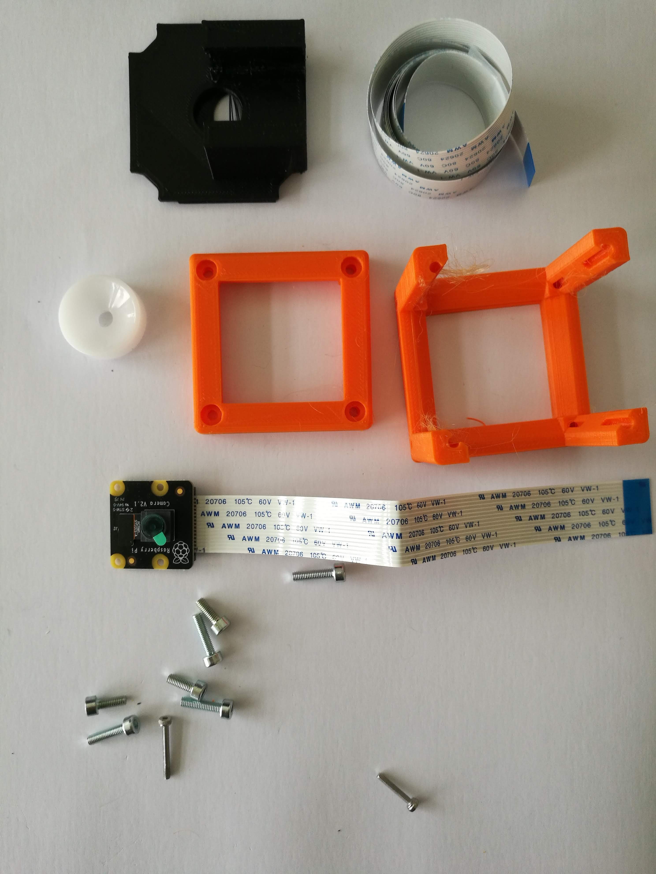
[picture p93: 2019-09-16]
WORKSHOP/MAKE_LIGHT_SHEET/ASSEMBLY_CUBE_RaspiCam_v2/IMAGES/CUBE_RASPICAM0.jpg

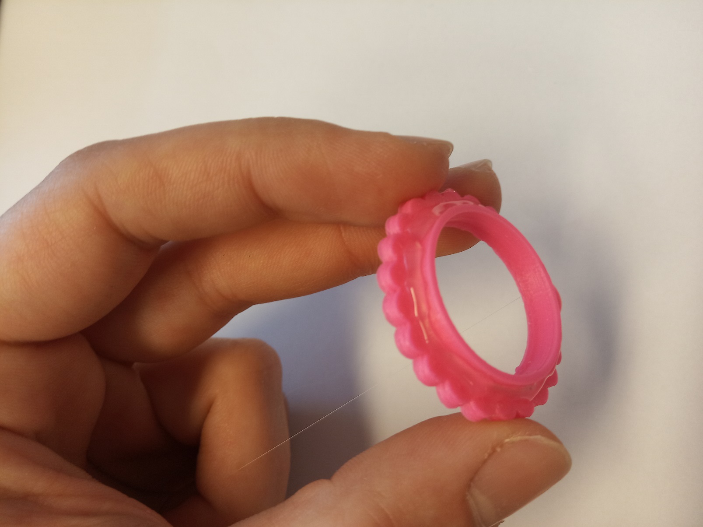
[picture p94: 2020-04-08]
WORKSHOP/MAKE_LIGHT_SHEET/ASSEMBLY_CUBE_Lens_v2/IMAGES/Lens_Holder_04.jpg

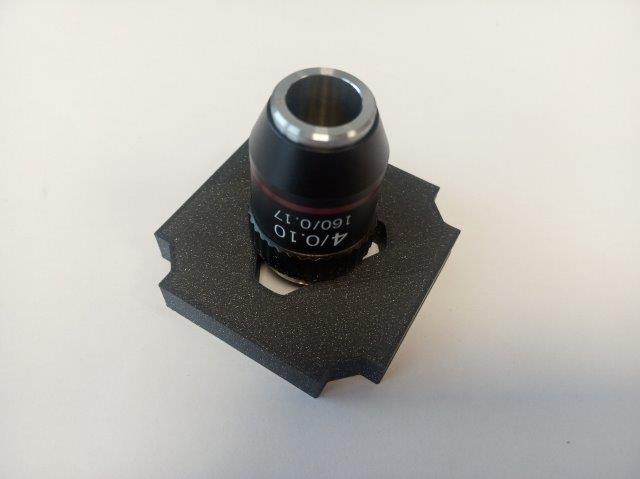
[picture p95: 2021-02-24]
CAD/ASSEMBLY_CUBE_Lens/IMAGES/CUBE_LENSHOLDER_02.jpg

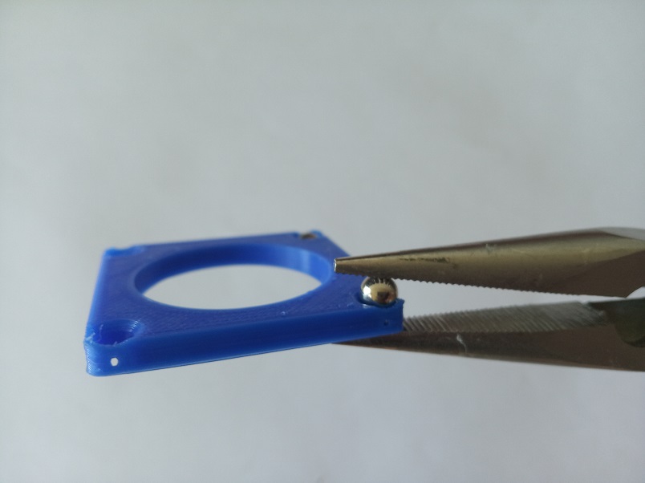
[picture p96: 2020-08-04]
CAD/ASSEMBLY_CUBE_Sample_Holder/IMAGES/Cube_Sampleholder_magnetic_05.jpg

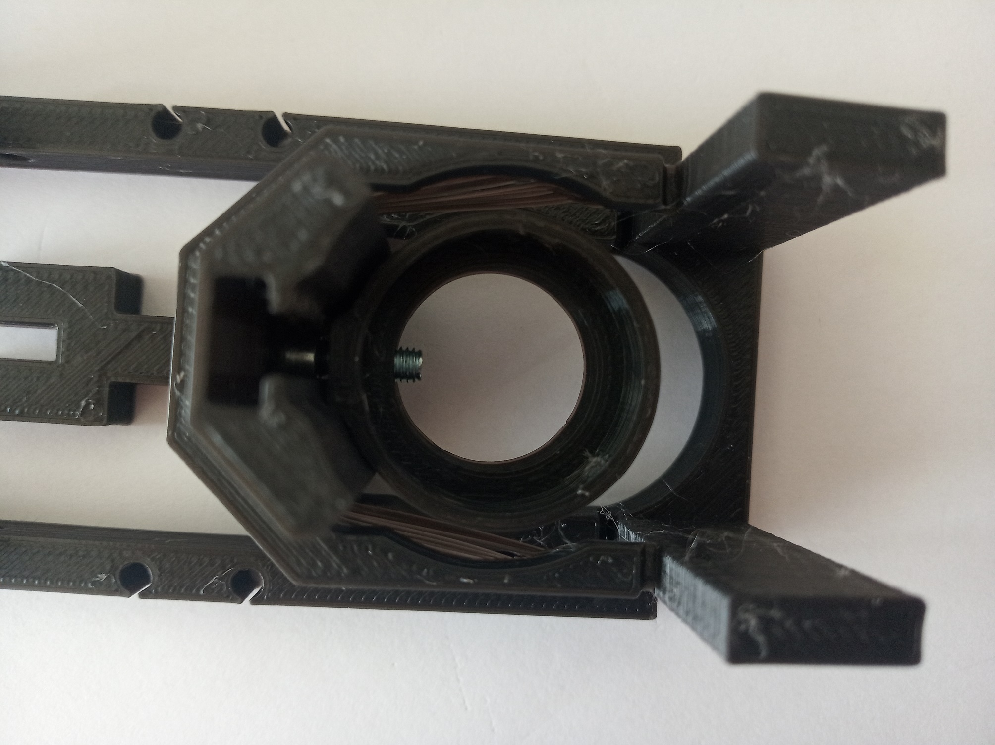
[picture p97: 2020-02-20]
WORKSHOP/MAKE_LIGHT_SHEET/ASSEMBLY_CUBE_Z-STAGE_v2/IMAGES/Z-stage_principle_01.jpg

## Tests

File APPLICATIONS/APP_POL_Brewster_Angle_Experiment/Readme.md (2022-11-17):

# Brewster Angle Experiment

<p align="center">
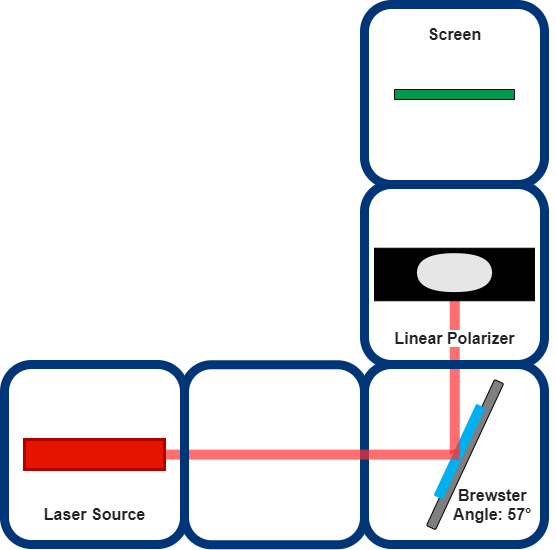
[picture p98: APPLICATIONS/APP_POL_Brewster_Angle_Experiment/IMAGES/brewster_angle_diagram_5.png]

</p>

There are several ways to produce polarized light. Optical processes reflection or refraction can be easily used to achieve that.  
When unpolarized light rays travel through a dielectric or insulating material, reflected and refracted light rays from the flat surface are mostly partially polarized.  
The amount of reflected light is specified by the optical properties of the reflecting surface, such as plastic sheets, glass, or highways.         
The incident angle of the incoming electromagnetic lightwave and refractive indices of media in which light travels through them have an essential role in the polarization degree of the reflected and refracted polarized light beams.

You can see the reflection and transmission of unpolarized light with most of the incident angle (𝜃) values below.

<p align="center">
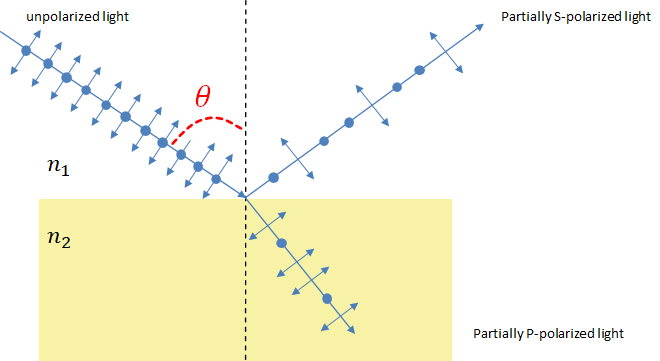
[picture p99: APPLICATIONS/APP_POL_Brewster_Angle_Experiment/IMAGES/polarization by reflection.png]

</p>

###### What is the Brewster angle?

When the incident ray travels from a less dense medium (n1) to a higher dense medium (n2) with a critical angle (𝜃_B), the reflected ray is perfectly s-polarized in which the orientation of the electric field vectors are perpendicular to the plane of incidence. Otherwise, the refracted beam has a 90-degree polarization angle, partially p-polarized. This critical angle is called a Brewster angle or polarization angle and is represented by 𝜃_B in the scheme below.

<p align="center">
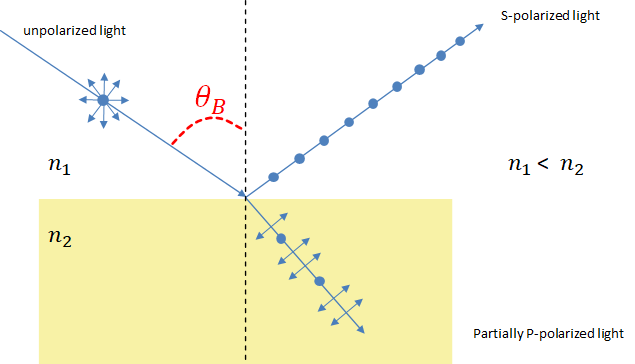
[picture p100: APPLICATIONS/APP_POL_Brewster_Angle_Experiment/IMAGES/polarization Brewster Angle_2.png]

</p>

Brewster angle can be easily calculated using refractive indices of traveling media of light. In our experiment, we used air (n1 = 1) as the first medium in which light comes first and reflects in this part and microscope slide glass (n2 = 1.5) as the second medium, and the light transmits through. When we calculate the Brewster angle for our experiment, it equals approximately 57 degrees, and we can find the equation below.  

<p align="center">


</p>

## Parts

### Modules for this setup

|  Name | Properties  |  Price | Link  | # |
|---|---|---|---|---|
|  4×4 Baseplate | Skeleton of the System |  21.79 €  | [Base-plate](../../CAD/ASSEMBLY_Baseplate)  | 1 |
|  MODULE:  *Polarizer Cube* | It holds the linearly polarizing filter  |  4.31 €  | [Linear Polarizer](../../CAD/ASSEMBLY_POL_Linear_Polarizer)  | 1 |
|  MODULE: *Kinematic Microscope Slide Holder* | It is used to insert the microscope slide with Brewster angle (53 degrees)  |  3.7 €  | [Microscope Slide Holder](../../CAD/ASSEMBLY_CUBE_Mirror_Kinematic_45)  | 1 |
|  MODULE: *Laser Cube* | LASER source holder  | 17.68 €  | [Light Source ](../../CAD/ASSEMBLY_CUBE_Laser)  | 1 |
|  EXTRA MODULE: Screen Holder Cube | It holds the Display Screen (Not Used in Practice) | 1 €  | [Screen](../../CAD/ASSEMBLY_CUBE_Sample_Holder)  | 1 |

### Parts to print

* 1 × [Base-plate 4×4](./STL/Assembly_Cube_Baseplate_4x4_v2.stl)
* 3 × [Cube base 1×1](./STL/10_Cube_1x1_v2.stl)
* 3 x [Cube lid 1×1](./STL/10_Lid_1x1_v2.stl)
* 1 × [Polarizer Guide](./STL/20_POL_Cube_Insert_Linear_Polarizer_Guide.stl)
* 1 × [Polarizer Wheel](./STL/20_POL_Cube_Insert_Linear_Polarizer_Wheel.stl)
* 1 × [Polarizer Lid](./STL/20_POL_Cube_Insert_Linear_Polarizer_Lid.stl)  
* 1 × [Kinematic Slide Holder - Base](./STL/20_POL_Cube_Insert_Brewster_Angle_Kinematic_Mount_Base_57_degrees.stl)
* 1 × [Kinematic Slide Holder - Plate](./STL/20_POL_Cube_Insert_Brewster_Angle_Kinematic_Mount_Plate_57_degrees.stl)
* 1 × [Kinematic Slide Holder - Clamp](./STL/20_POL_Cube_Insert_Brewster_Angle_Kinematic_Mount_Clamp_57_degrees.stl)
* 2 × [Laser Holder](./STL/20_Cube_Insert_Laser_Holder_v2.stl)
* 1 x [Laser Clamp](./STL/00_Laser_Clamp_OnOffSwitch.stl)         
__*Extra Holder Parts but NOT USED in our experiment:*__
* 1 x [Sample Holder - comb](./STL/20_Cube_Sampleholder.stl)

<p align="center">
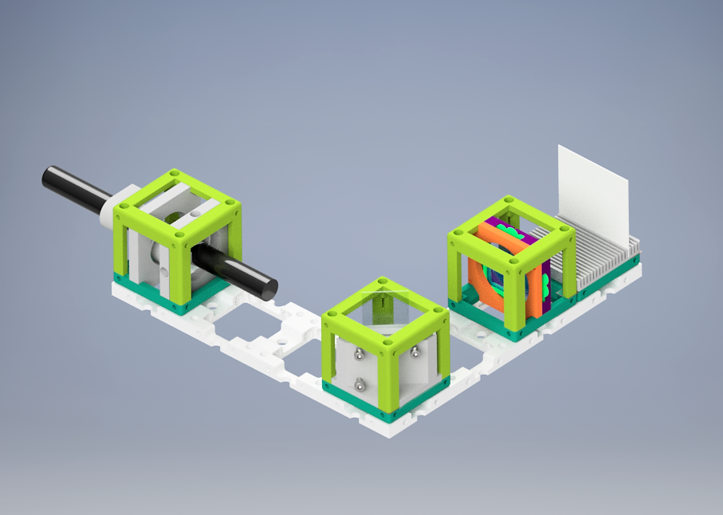
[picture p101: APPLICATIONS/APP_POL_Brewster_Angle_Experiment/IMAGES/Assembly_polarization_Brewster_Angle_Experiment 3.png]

</p>  

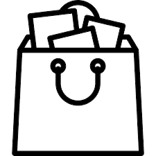
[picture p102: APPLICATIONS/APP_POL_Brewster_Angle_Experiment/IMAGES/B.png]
##  Additional components
* Check out the [RESOURCES](../../TUTORIALS/RESOURCES) for more information!
* 1 × Linear Polarizing Sheet [🢂](https://amazon.de/-/en/Polarizing-A4-Sheet-Polarizer-Educational-Polarized/dp/B06XWXRB75/ref=pd_sbs_421_3/262-2115536-7173904?_encoding=UTF8&pd_rd_i=B06XWXRB75&pd_rd_r=b88e7340-b061-4e0b-8daa-8ec533fd7c71&pd_rd_w=qlkAY&pd_rd_wg=At9EZ&pf_rd_p=a03ac387-6e4d-4f6b-96b6-1853da0bb37b&pf_rd_r=49HX2Z4Q5KRZSQ2FWRQR&psc=1&refRID=49HX2Z4Q5KRZSQ2FWRQR)
* 67 × 5 mm Ball magnets [🢂](https://www.magnetladen.de/kugelmagnet-5-mm-n42-nickel/)
* 28 x Screws DIN912 ISO 4762 - M3×12 mm [🢂](https://eshop.wuerth.de/Zylinderschraube-mit-Innensechskant-SHR-ZYL-ISO4762-88-IS25-A2K-M3X12/00843%20%2012.sku/de/DE/EUR/)
* 3 x Screws DIN912 ISO 4762 M2×16 mm [🢂](https://www.amazon.de/Edelstahl-Sechskopf-Knopf-Schrauben-Unterlegscheiben-Sortiment-Aufbewahrung/dp/B073SS7D8J/ref=sr_1_fkmr0_1?__mk_de_DE=%C3%85M%C3%85%C5%BD%C3%95%C3%91&keywords=zylinderkopfschrauben+set+galvanisiert&qid=1565007371&s=diy&sr=1-1-fkmr0)
* Microscope Rectangular Coverslips [🢂](https://www.ebay.de/itm/223260964391?hash=item33fb63f627:g:pukAAOSwsGpb%7E14N)
* 1 × 5 mW Blue UV Laser Pointer [🢂](https://www.laserlands.net/5mw-450nm-blue-laser-pointer-pen.html)

<p align="center">
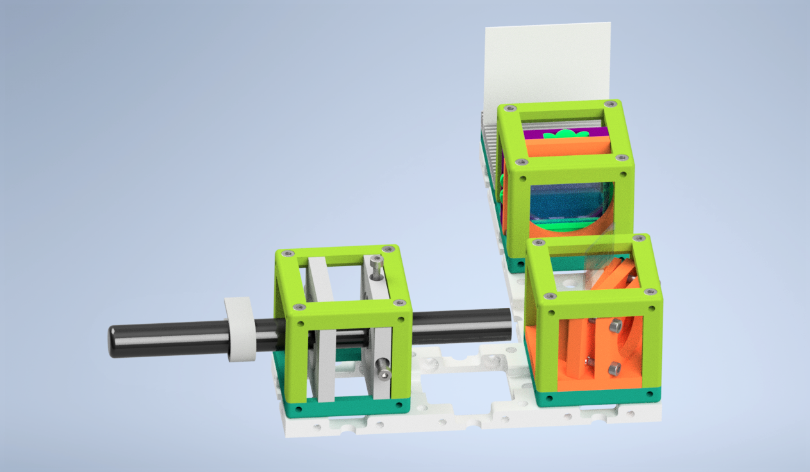
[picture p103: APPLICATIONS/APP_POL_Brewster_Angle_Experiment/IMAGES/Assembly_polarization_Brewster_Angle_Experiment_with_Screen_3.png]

</p>

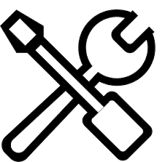
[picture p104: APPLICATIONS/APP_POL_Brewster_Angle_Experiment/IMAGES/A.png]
##  Assembly

* [Baseplate](../../CAD/ASSEMBLY_Baseplate)
* [Linear Polarizer Cube](../../CAD/ASSEMBLY_POL_Linear_Polarizer)
* [Microscope Slide Holder Cube](../../CAD/ASSEMBLY_CUBE_Mirror_Kinematic_45) : Brewster Angle Cube has same assembling procedure with Kinematic Mirror Holder 45 degrees.
* [LASER Holder Cube](../../CAD/ASSEMBLY_CUBE_Laser)   
__*EXTRA MODULES:*__
* [Sample Holder for Screen](../../CAD/ASSEMBLY_CUBE_Sample_Holder)

All necessary parts to assemble a Microscope Slide Glass Holder Module be gathered in the image below:

<p align="center">
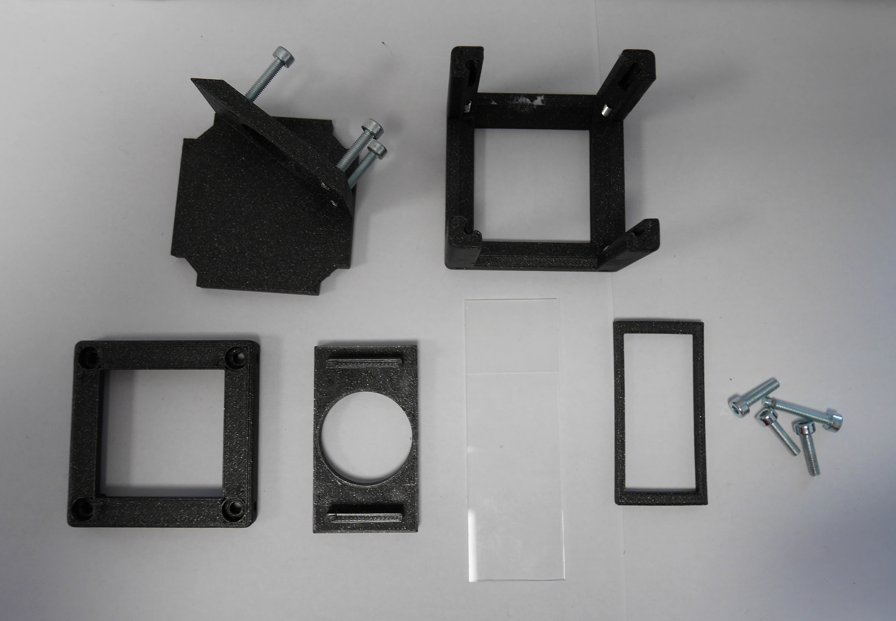
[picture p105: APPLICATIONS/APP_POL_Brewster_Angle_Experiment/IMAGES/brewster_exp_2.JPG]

</p>

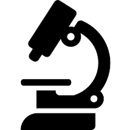
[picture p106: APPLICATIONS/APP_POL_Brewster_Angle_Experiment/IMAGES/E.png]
##  Results

Brewster's angle experiment setup can be prepared easily. After printing and assembling the module parts, we try to find a critical angle or Brewster's angle as much as we can.

<p align="center">
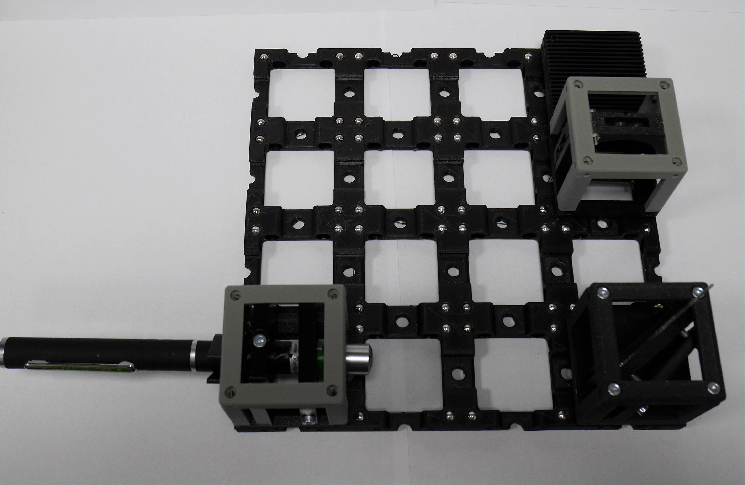
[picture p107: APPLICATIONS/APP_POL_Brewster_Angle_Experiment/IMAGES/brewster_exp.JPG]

</p>

In this setup, we use LASER as a light source because it is easier to observe the polarization degree changes by reflection. As a first step, LASER light beams reflect from microscope slide glass and pass through a linear polarizer. Then a piece of paper is inserted on the sample holder comb. Finally, we can observe the totally polarized reflected light.

<p align="center">

</p>

We should make a good alignment to find the Brewster angle as the incidence angle of the incoming light. In practice, it is hard because of using screws, we could not find the exact incidence angle of a microscope slide. Nevertheless, I could take results that are almost perfectly polarized light after reflection in almost critical angle.   
You can see the reflected laser light beam without alignment at a random incident angle above.

In the image below, the incoming beam is reflected with almost Brewster angle, 57 degrees for microscope slide glass:

<p align="center">

</p>

Let's look at our almost perfectly polarized light by reflection experiment video records. The orientation direction of the linear polarizer only changes in 1st and 2nd videos, and we see that reflected light is totally polarized almost.  The light is blocked, and we can see almost no light after the polarizer when the orientation of the linear polarizer is perpendicular to the polarization orientation of the reflected beam.

<p align="center">

</p>

<p align="center">

</p>

## New Ideas
We are open to new ideas. Please contribute to the project freely, this place is a free country which is built by codes and machines :robot:

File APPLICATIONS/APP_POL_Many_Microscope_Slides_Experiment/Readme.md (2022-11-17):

# Many Microscope Slides Experiment

<p align="center">

</p>

There are different ways of producing polarized light from unpolarized light.  In an example process: light travels from medium 1 to medium 2. Some part of the incident light reflects from the surface of medium 2. This reflected light can be partially polarized light or totally polarized light in the Brewster angle. Another part of the initial light is refracted to medium 2 as a partially polarized light. You can have more detailed information about the polarization of the light by reflection  [in the Brewster Angle Experiment](../../APPLICATIONS/APP_POL_Brewster_Angle_Experiment).

However, transmission light eventually polarizes based on the polarization by reflection, when the light is transmitted many times through several microscope slides.

In the experiment, a medium is constructed with 7 adjacent microscope slides by the experimenter. Then, unpolarized light rays travel through microscope slides. After this glass medium, many times transmitted rays will be polarized. If we transmit light through only one microscope slide, refracted light will be partially polarized. But if we repeat this process many times such as 7 or more times, in one point transmitted light will be perfectly polarized.

<p align="center">

</p>

*Polarization by Refraction:* Unpolarized or partially polarized incoming light travels, reflects as partially s polarized and transmits as partially p polarized between medium 1and medium 2.

## Parts

### Modules for this setup

|  Name | Properties  |  Price | Link  | # |
|---|---|---|---|---|
|  4×1 Baseplate | Skeleton of the System | 5.47 €  | [Base-plate](../../CAD/ASSEMBLY_Baseplate)  | 1 |
|  MODULE:  *Polarizer Cube* | It holds the linearly polarizing filter  |  4.31 €  | [Linear Polarizer](../../CAD/ASSEMBLY_POL_Linear_Polarizer)  | 1 |
|  MODULE: *Many Microscope Slides Holder* | It hold 7 or more microscope slides back to back  | 2.11 €  | [Slides Holder](../../CAD/ASSEMBLY_CUBE_Sample_Holder)  | 1 |
|  MODULE: *Laser Cube* | LASER source holder  | 17.68 €  | [Light Source ](../../CAD/ASSEMBLY_CUBE_Laser)  | 1 |
|  EXTRA MODULE: Screen Holder Cube | It holds the Display Screen (Not Used in Practice) | 1 €  | [Screen](../../CAD/ASSEMBLY_CUBE_Sample_Holder)  | 1 |

### Parts to print

* 1 × [Base-plate 4×4](./STL/Assembly_Cube_Baseplate_4x1_v2.stl)
* 2 × [Cube base 1×1](./STL/10_Cube_1x1_v2.stl)
* 3 x [Cube lid 1×1](./STL/10_Lid_1x1_v2.stl)
* 1 × [Polarizer Guide](./STL/20_POL_Cube_Insert_Linear_Polarizer_Guide.stl)
* 1 × [Polarizer Wheel](./STL/20_POL_Cube_Insert_Linear_Polarizer_Wheel.stl)
* 1 × [Polarizer Lid](./STL/20_POL_Cube_Insert_Linear_Polarizer_Lid.stl)
* 1 x [Many Microscope Slides Holder](./STL/20_Cube_Sampleholder.stl)
* 2 × [Laser Mount](./STL/20_Cube_Insert_Laser_Holder_v2.stl)
* 1 x [Laser Clamp](./STL/00_Laser_Clamp_OnOffSwitch.stl)   

<p align="center">

</p>  

##  Additional components
* Check out the [RESOURCES](../../TUTORIALS/RESOURCES) for more information!
* 1 × Linear Polarizing Sheet [🢂](https://amazon.de/-/en/Polarizing-A4-Sheet-Polarizer-Educational-Polarized/dp/B06XWXRB75/ref=pd_sbs_421_3/262-2115536-7173904?_encoding=UTF8&pd_rd_i=B06XWXRB75&pd_rd_r=b88e7340-b061-4e0b-8daa-8ec533fd7c71&pd_rd_w=qlkAY&pd_rd_wg=At9EZ&pf_rd_p=a03ac387-6e4d-4f6b-96b6-1853da0bb37b&pf_rd_r=49HX2Z4Q5KRZSQ2FWRQR&psc=1&refRID=49HX2Z4Q5KRZSQ2FWRQR)
* 16 × 5 mm Ball magnets [🢂](https://www.magnetladen.de/kugelmagnet-5-mm-n42-nickel/)
* 24 x Screws DIN912 ISO 4762 - M3×12 mm [🢂](https://eshop.wuerth.de/Zylinderschraube-mit-Innensechskant-SHR-ZYL-ISO4762-88-IS25-A2K-M3X12/00843%20%2012.sku/de/DE/EUR/)
* 3 x Screws DIN912 ISO 4762 M2×16 mm [🢂](https://www.amazon.de/Edelstahl-Sechskopf-Knopf-Schrauben-Unterlegscheiben-Sortiment-Aufbewahrung/dp/B073SS7D8J/ref=sr_1_fkmr0_1?__mk_de_DE=%C3%85M%C3%85%C5%BD%C3%95%C3%91&keywords=zylinderkopfschrauben+set+galvanisiert&qid=1565007371&s=diy&sr=1-1-fkmr0)
* 9 x Microscope Rectangular Coverslips [🢂](https://www.ebay.de/itm/223260964391?hash=item33fb63f627:g:pukAAOSwsGpb%7E14N)
* 1 × 5 mW Blue UV Laser Pointer [🢂](https://www.laserlands.net/5mw-450nm-blue-laser-pointer-pen.html)

<p align="center">

</p>  

##  Assembly

* [Baseplate](../../CAD/ASSEMBLY_Baseplate)
* [Linear Polarizer Cube](../../CAD/ASSEMBLY_POL_Linear_Polarizer)  
* [Microscope Slides Holders](../../CAD/ASSEMBLY_CUBE_Sample_Holder)   
* [LASER Holder Cube](../../CAD/ASSEMBLY_CUBE_Laser)    
__*EXTRA MODULES:*__
* [Sample Holder for Screen](../../CAD/ASSEMBLY_CUBE_Sample_Holder)

<p align="center">

</p>  

##  Results

We printed and assembled Many Microscope Slides Experiment modules parts. Then, we bought the necessary components and inserted them into the cubes.         
The printed and assembled Sample Holder Comb module with nine microscope glasses:

<p align="center">

</p>

You will find the basic version of the experiment without a Screen adn Linear Polarizer module below.

<p align="center">

</p>

Images of the resulting experimental setup;     
side view (top) , top view (bottom)

<p align="center">

</p>

<p align="center">

</p>

We can observe the direct effect of the rotational angle of the linear polarizer in the video below. Laser light travels to microscope slides and air gap media several times and gets close to fully polarized light.  We can see this effect eith adding Linear Polarizer cube.       
The intensity of passing light through linear polarizer  changes when the direction angle of the polarization filter changes 360 degrees.     

We can see the change with two videos below. They demonstrates the experiment from two different views.

<p align="center">

</p>

<p align="center">

</p>

## New Ideas

Rat-Tat! We are here to hear new ideas. Please don't shy and have a heart-to-heart talk with us.  :gift_heart:

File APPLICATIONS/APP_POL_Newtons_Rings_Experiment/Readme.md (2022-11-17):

# Newton's Rings Experiment

<p align="center">

</p>

Soap bubbles, oil slicks, or oxidized metal surfaces can create interference patterns under the white light illumination. In Newton's fringes, light reflects as a constructively or destructively interfered when the light waves travel through two surfaces. These combinations can be created using glass-air or air-glass contacts. These two interferences generate a concentric ring pattern of rainbow colours in white light illumination. In the same way, monochromatic light creates dark-light rings.    

The simplest example can be made using two well-cleaned microscope slides as interfaces. Air film is enclosed between two slides inconsistently, and irregular-coloured fringes are generated under the daily light. When the pressure on the microscope slides changes, fringes move and change.

In the Newton's Rings Experiment, we used a convex lens whose surface is placed on an optical plane glass, a microscope glass, from its long focal length side. These two pieces are held together with non-uniform thin air film. After light illumination through these surfaces,the air gap and random pressures on the microscope slide and plano-convex lens cause the generation of irregular coloured or single-colour fringes; Newton's Rings.

#### The details of Experiment Modules

Linear Polarizer is used in this experiment to visualize the polarization change of reflected lights from two media on the interference pattern.

Additional module design was made for combining the microscope glass slide and plano-convex lens inside one cube insert. You can see rendered image of the Newton's Rings Lens-Slide Holder Module from Inventor.  

<p align="center">

</p>

We used laser as a light souce in the setup. During the experiment, we extended beam size of the pen laser from 2 mm to 6 mm using a regular [Beam Expander Module](../../CAD/ASSEMBLY_CUBE_Beamexpander).

## Parts

### Modules for this setup

|  Name | Properties  |  Price | Link  | # |
|---|---|---|---|---|
|  4×4 Baseplate | Skeleton of the System |  21.79 €  | [Base-plate](../../CAD/ASSEMBLY_Baseplate)  | 1 |
|  MODULE: *Beam Expander Cube* | It expands the laser beam size  |  13.55 €  | [Beam Expander](../../CAD/ASSEMBLY_CUBE_Beamexpander)  | 1 |
|  MODULE: *Beam Splitter Cube* | It splits the incoming beam and recombine them  |  29.17 €  | [Beam Splitter Holder](../../CAD/ASSEMBLY_CUBE_Beamsplitter)  | 1 |
|  MODULE: *Newton's Rings Slide-Lens Holder Cube* | It creates Newton's Rings  | 7.54 €  | [Lens - Slide Holder](../../CAD/ASSEMBLY_POL_Newtons_Rings_Module )  | 1 |
|  MODULE:  *Polarizer Cube* | It holds the linearly polarizing filter  |  4.31 €  | [Linear Polarizer](../../CAD/ASSEMBLY_POL_Linear_Polarizer)  | 1 |
|  MODULE: *Laser Cube* | LASER source holder  | 17.68 €  | [Light Source](../../CAD/ASSEMBLY_CUBE_Laser)  | 1 |
|  EXTRA MODULE: Screen Holder Cube | It holds the Display Screen (Not Used in Practice) | 1 €  | [Screen](../../CAD/ASSEMBLY_CUBE_Sample_Holder)  | 1 |

### Parts to print

* 1 × [Base-plate 4×4](./STL/Assembly_Cube_Baseplate_4x4_v2.stl)
* 5 × [Cube base 1×1](./STL/10_Cube_1x1_v2.stl)
* 6 x [Cube lid 1×1](./STL/10_Lid_1x1_v2.stl)
* 1 x [Beam Expander Holder](./STL/20_Cube_Insert_Beamexpander_astromedia_v3.stl)
* 1 × [Beam Splitter Cube Holder](./STL/20_Cube_Insert_Beamsplitter.stl)
* 1 × [Newton's Rings - Lens & Slide Holder](./STL/20_POL_Cube_Insert_Newtons_Rings_LensHolder.stl)
* 1 × [Newton's Rings - Lens & Slide Holder Clamp](./STL/20_POL_Cube_Insert_Newtons_Rings_Lens_Clamp.stl)
* 2 × [Laser Holder](./STL/20_Cube_Insert_Laser_Holder_v2.stl)
* 1 x [Laser Clamp](./STL/00_Laser_Clamp_OnOffSwitch.stl)
* 1 × [Polarizer Guide](./STL/20_POL_Cube_Insert_Linear_Polarizer_Guide.stl)
* 1 × [Polarizer Wheel](./STL/20_POL_Cube_Insert_Linear_Polarizer_Wheel.stl)
* 1 × [Polarizer Lid](./STL/20_POL_Cube_Insert_Linear_Polarizer_Lid.stl)        
__*Extra Holder Parts but NOT USED in our experiment:*__
* 1 x [Sample Holder - comb](./STL/20_Cube_Sampleholder.stl)

<p align="center">

</p>  

##  Additional components
* Check out the [RESOURCES](../../TUTORIALS/RESOURCES) for more information!
* 1 × Linear Polarizing Sheet [🢂](https://amazon.de/-/en/Polarizing-A4-Sheet-Polarizer-Educational-Polarized/dp/B06XWXRB75/ref=pd_sbs_421_3/262-2115536-7173904?_encoding=UTF8&pd_rd_i=B06XWXRB75&pd_rd_r=b88e7340-b061-4e0b-8daa-8ec533fd7c71&pd_rd_w=qlkAY&pd_rd_wg=At9EZ&pf_rd_p=a03ac387-6e4d-4f6b-96b6-1853da0bb37b&pf_rd_r=49HX2Z4Q5KRZSQ2FWRQR&psc=1&refRID=49HX2Z4Q5KRZSQ2FWRQR)
* 64 × 5 mm Ball magnets [🢂](https://www.magnetladen.de/kugelmagnet-5-mm-n42-nickel/)
* 44 x Screws DIN912 ISO 4762 - M3×12 mm [🢂](https://eshop.wuerth.de/Zylinderschraube-mit-Innensechskant-SHR-ZYL-ISO4762-88-IS25-A2K-M3X12/00843%20%2012.sku/de/DE/EUR/)
* 3 x Screws DIN912 ISO 4762 M2×16 mm [🢂](https://www.amazon.de/Edelstahl-Sechskopf-Knopf-Schrauben-Unterlegscheiben-Sortiment-Aufbewahrung/dp/B073SS7D8J/ref=sr_1_fkmr0_1?__mk_de_DE=%C3%85M%C3%85%C5%BD%C3%95%C3%91&keywords=zylinderkopfschrauben+set+galvanisiert&qid=1565007371&s=diy&sr=1-1-fkmr0)
* 1 x Beamsplitter Cube (Art. 2137) [🢂](https://optikbaukasten.de/)
* 1 x Microscope Rectangular Coverslips [🢂](https://www.ebay.de/itm/223260964391?hash=item33fb63f627:g:pukAAOSwsGpb%7E14N)
* 1 x Plano-Convex Lens [🢂](https://www.comaroptics.com/components/lenses/simple-convex-lenses/plastic-lenses)
* 1 × 5 mW Blue UV Laser Pointer [🢂](https://www.laserlands.net/5mw-450nm-blue-laser-pointer-pen.html)
* 1 x iPhone 5 Lens f'=3mm (separated from an iPhone camera spare part) [🢂](https://www.ebay.com/itm/172395994496)
* 1 x Achromat Lens f' = 26,5 mm [🢂](https://pgi-shop.de/achromat-2-lens-oe-15-mm-f-26.5-mm/)

<p align="center">

</p>  

##  Assembly

* [Baseplate](../../CAD/ASSEMBLY_Baseplate)
* [Beam Expander Cube](../../CAD/ASSEMBLY_CUBE_Beamexpander)
* [Beam Splitter Cube](../../CAD/ASSEMBLY_CUBE_Beamsplitter)
* [Newton's Rings Slide-Lens Holder Cube](../../CAD/ASSEMBLY_POL_Newtons_Rings_Module)
* [Linear Polarizer Cube](../../CAD/ASSEMBLY_POL_Linear_Polarizer)
* [LASER Holder Cube](../../CAD/ASSEMBLY_CUBE_Laser)   
__*EXTRA MODULES:*__
* [Sample Holder for Screen](../../CAD/ASSEMBLY_CUBE_Sample_Holder)

##  Results

We started with building of UC2 Modules: design, print, assemble and be ready for testing. You can see our Beam Expander Cube on the 4x1 Baseplate below.

<p align="center">

</p>

Lens - Slide Holder Module is the key element for the generation of Newton's Rings. Necessary Module parts are shown in the image below.

<p align="center">

</p>

Assembled and Ready-To-Use module should look like ...

<p align="center">

</p>

***The experimental procedure*** begins with
* installation the Laser and Beam Expander Modules on the 4x4 Baseplate.

<p align="center">

</p>

* After checking the expansion of the laser beam width, Beam Splitter Cube is added to the setup.

<p align="center">

</p>

* One of the divided incoming beams is directed to the Newton's Rings Lens & Microscope Holder cube, and light reflects from the convex lens-plate glass combination through the beam splitter cube, then on observation screen.

<p align="center">

</p>

<p align="center">

</p>

Demonstrating the experiment is much easier with a laser light source and results in visible fringes. The Newton's Fringes will vary in colour from inner to outer circles if a white light source is replaced with a laser source.

Let's zoom in Newton's Fringes with more experiment images!

<p align="center">

</p>

The effect of the polarization angle change of the Linear Polarizer Filter can be seen in the video.

<p align="center">

</p>

## New Ideas
We are open to new ideas. Please contribute to the project freely, this place is a free country which is built by codes and machines :robot:

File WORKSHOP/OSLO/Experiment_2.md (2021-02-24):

## Experiment – 2
Build a device to see the effect of Fourier-filtering (e.g. "ABBE-Experiment")

The idea is to see the effect of Fourier filtering during image formation by placing an aperture inside the back focal plane (BFP) of the imaging lens.

All information about the setup can be found [here](../../APPLICATIONS/APP_Abbe_Setup)

## Steps

First of all you have to fuse two boxes since you need more optical elements than a single box can provide. So fuse with your neighbor

1. Look for the right lenses which have a focal-length of ~40-50mm
2. Align the illumination: Take the LED-module (blue) and a lens which collimates it
3. Take the sample mount (looks like comp) and place it right after the first lens so that the sample gets illuminated by the illumination
4. Take a second lens as the imaging lens so that the sample is roughly within the focal plane of it
5. Now take the beam-splitter cube and place it directly behind the comb-like cube
6. Two additional lenses have to be placed after the BS-cube to form an image and access the Fourier plane on two different cameras (have a look at the figure from the link above)
7. Turn on the Raspberry PI where you have connected the Cameras and start the camera using: ```raspistill -k```for constant-mode from the Raspberry PI Terminal
8. Taking image can be achieved by doing the following steps:
	- go to home-folder ```cd ./data```
	- take images using ```raspistill -o myimage_1.jpg```where ```myimage_1``` is a name of your choice

## Tasks

First think about what could happened; Does this go hand-in-hand of what happens in the experiment? :-)

- Vary illumination source shape by taking aluminum foil and stitch different patterns in it to vary the degree of coherence
	- What happens on the Fourier-cam?
- Take a piece of paper and place it in the BFP of the imaging lens, try different shapes.
	- What happens to the image on the raspberry pi camera?

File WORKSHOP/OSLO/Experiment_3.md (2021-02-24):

## Experiment – 3 (Incubator Microscope)
Assemble and setup the incubator microscope

This experiment sets up a compound microscope in order to get familiar with the GUI running on the Raspberry Pi.
The experiment involves multiple MQTT-able components such as the ```LED-Array``` and the ```Z-stage```.

The microscope is based on the design found [here](../../APPLICATIONS/APP_Incubator_Microscope)

## Steps

1. Setup the microscope using one BOX and the description given in the link above
2. First try to get an image using the ```raspistill -k``` command in combination with your cellphone torch
3. Setup the WiFi-connection:
	- Optional: Install the UC2 Wifi-APP for controlling the components from [here](https://github.com/bionanoimaging/UC2-Software-GIT/tree/master/GUI/Android/UC2-TheBox)
4. Setup the Raspberry Pi with the Camera and start the GUI by double-clicking on the UC2-icon which appears on the desktop
5. Get familiar with basic functions inside the GUI
6. Try to change the LED-Matrix pattern using the customized settings
7. Try to get a focussed microscope image by coarsely aligning the lens and stepping it up-and-down using the GUI
8. Try to set up a time-series using the GUI
9. Place a sample in the tray and study how the contrast varies when the light-source changes

### Long-Time Experiment

Prepare a "living" sample and observe it over-night:

#### DOG-sample

Ask Edna ;-)

#### YEAST-sample

***Ingredients***
- 10 g/L Yeast extract (powder)
- 20 g/L peptone
- 20 g/L glucose

*alternatively*
- 4 g/L NH4H2PO4 = N source
- 10 g/L glucose
- 2 g/L Yeast extract
- 4 g/L peptone

*alternatively*
- ready Medium YNB
- 10 g/L Glucose

*alternatively*
- Fruit juice with N-source
- or nutrient salts for wine production you can get this in the pharmacy or health food store or drugstore.

**Tips:**

- pH-value should be between 5 and 7 - instead of glucose you can also take sucrose.
- Yeast forms ethanol - gas development
- Yeast cannot metabolize starch (flour) and starch grains are visible under the microscope.

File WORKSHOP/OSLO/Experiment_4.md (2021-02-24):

## Experiment – 4 Light sheet Microscope
This time we want to build the light sheet microscope.

The basic description about the device and how to align it can be found [here](../../APPLICATIONS/APP_LIGHTSHEET_Workshop).

## Tasks

1. Mount a sample on the *S-Stage*
2. Perform a Z-stack of the sample
3. Load the images/videos to Fiji and create a Z-project

## RESULT

Larvae of fruit fly using a 4x lens for detection and illumination.

<p align="center">

</p>

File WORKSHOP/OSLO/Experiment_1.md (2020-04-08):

## Experiment – 1 (Telescope)
Build your own telescope and verify magnification

This experiment is an introduction into the UC2 toolbox and should give you a chance to get familiar with the core-idea of creating simple, but also complex optical setups using the modular system.

### Steps

1. Find the proper manual for the telescope(s) on the UC2 github-page

	HINTS:

	- [TheBOX](../../TheBOX/FullBOX)
	- [CAD Applications](../../APPLICATIONS)

2. Take the box, find the components you need and assemble the telescope(s)

	HINTS:

	- Take the proper lenses for the corresponding magnification
	- Try to achieve the Keplerian and Galilean Telescope
	- Eventually exchange the components inside the cube

3. Once you have completed building one of the telescope(s), take your cellphone and measure the magnification of the telescope. This can be done with a reference object with known dimensions at a far-away distance (e.g. door, 2m and 3m away). Take a picture with and without the telescope. 

4. Measure the ratio of the magnified reference sample (magnified/non-magnified) and the orientation of the sample using Fiji on your computer. Is it the value you expected?

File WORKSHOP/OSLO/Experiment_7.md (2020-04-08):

## Experiment – 7 Smartphone Microscope
This time we want to build the smartphone microscope combined with image processing

The basic description about the device and how to align it can be found [here](../../APPLICATIONS/APP_SMARTPHONE_MICROSCOPE).

## Tasks

1. Mount a sample on the *Z-Stage*
2. Take a picture
3. Send it to ImJoy
4. Process it and see the result

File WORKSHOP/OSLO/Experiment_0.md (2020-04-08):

## Experiment – 0
Get familiar with ```TheBOX```

This experiment should give you an impression of what's inside the box and what can be achieved with it.
Just go through the UC2-Github and get familiar with the project. Please complain if you find errors!

HINTS:

* [TheBOX on Github](../../TheBOX/FullBOX)

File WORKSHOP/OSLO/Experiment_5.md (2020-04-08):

## Experiment – 4 Examination of the Time-Lapse Series
Process long-time series with Software of choice

The over-night measurements using the incubator microscope can be processed using e.g. Fiji or Python. Try to connect to the microscope using a "SSH" tool (e.g. [WinSCP for Windows](https://winscp.net/eng/index.php) or [Cyber Duck for MAC](https://cyberduck.io/)

Connect to the device with an IP-address of either
```
21.3.2.102 - setup 9

21.3.2.112

21.3.2.122

21.3.2.132

21.3.2.142
```

The files can be found in the folder ```/home/uc2/UC2/UC2-GUI/data/20200120/```. Take the newest date (not necessarily the actual date) and look through the ```expt_0**```folders. The one with many images can be copied on your local machine (takes some time).

**ALTERNATIVE:** You can also copy the files using a USB drive (takes even longer).

## STEPS:

1. Import an image sequence using the Fiji Import command
2. Split the color channels and use only the green one
3. Bin the pixels by a factor of 6
4. Export the stack as a ```.tiff```-file

The result could look like this here (30 minutes of MDCK-cells prepared by Edna and Kay):

<p align="center">

</p>

5. Process the data with your preferred image processing pipe-line (e.g. tracking, segmentation, etc.)
6. Publish the result somewhere :)

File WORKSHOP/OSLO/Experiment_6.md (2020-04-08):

# Experiment 5 - Intro to Image Processing with ImJoy
Simple example on how to use ImJoy

This tutorial gives you an idea on how to operate a simple image processing task with your cellphone as a camera for a microscope and [ImJoy](https://imjoy.io) as the cloud-based software.

We provide a sample script in our [UC2 ImJoy Repository](https://github.com/bionanoimaging/UC2-ImJoy-Plugins) which you can fork and modify.
The file of interest is called ```UC2_tools_janelia.imjoy.html```

During this work you will learn how to load an image through the web-interface and perform a basic edge-detection task which gets displayed in the browser.

## Start the ImJoy Server (only for Admin)

After installing ImJoy Server following [this tutorial](https://imjoy.io) a https-tunnel has to be established using telebit. Follow the steps mentioned [here](https://telebit.cloud/). Setup an account and start the server using:

```
~/telebit http 9527

telebit restart - stops connection
```

It forwards the port **9527** which is now visible to the public (!).

Go to [https://imjoy.io](https://imjoy.io) and start ImJoy

<p align="center">

</p>

Hit the "Start ImJoy" button and click "+ Plugins" on the left hand-side

<p align="center">

</p>

add the UC2-repo: [https://github.com/bionanoimaging/UC2-ImJoy-Plugins](https://github.com/bionanoimaging/UC2-ImJoy-Plugins) in "Install from the plugin repository" and hit enter:

<p align="center">

</p>

Click on the cloud-symbol next to "UC2 Janelia Workshop" to install the plugin.

We need to add the Plugin engine for the computationally expensive algorithms:

<p align="center">

</p>

Click on "Add new Plugin engine(#)" and add this:
[https://honest-otter-XX.telebit.io/](https://honest-otter-98.telebit.io/) and the Token: ```bf50b0cd-5123-46a6-9984-a6b8860fc7c5```

Now you can execute all plugins either on the cellphone or the laptop:

## Tutorial to install the plugins

1.) Go to:

•	[https://imjoy.io/#/app](https://imjoy.io/#/app)

2.) Add Computing Engine using the rocket-symbol; select “another Computer” and enter the URL (replace XX with given my UC2):

•	[https://honest-otter-XX.telebit.io/](https://honest-otter-98.telebit.io/)

3.) Enter Token:

•	bf50b0cd-5123-46a6-9984-a6b8860fc7c5

4.) Add UC2-ImJoy Plugin Repository (paste and hit enter)
•	[https://github.com/bionanoimaging/UC2-ImJoy-Plugins](https://github.com/bionanoimaging/UC2-ImJoy-Plugins)

5.) Select „UC2 Janelia Workshop“ by clicking on the cloud to install it

6.) In the side-bar select “UC2 Janelia Workshop”

6.) Select any image and upload it

7.) Wait and keep your fingers pressed
###

## Code

### GUI

The following code can be found in the GUI-file: ```UC2_GUI_UploadDemo.imjoy```

**JSON**
This handles the GUI settings for the ImJOY backend and the libraries necessary to deal with loading data and save it to the local server:

```
<config lang="json">
{
  "name": "UC2 Upload Demo",
  "type": "window",
  "tags": [],
  "ui": "",
  "version": "0.1.0",
  "cover": "",
  "description": "[This describes how to upload and process an image through the GUI.]",
  "icon": "extension",
  "inputs": null,
  "outputs": null,
  "api_version": "0.1.2",
  "env": "",
  "permissions": [],
  "requirements": [
    "https://unpkg.com/axios/dist/axios.min.js",
    "https://unpkg.com/spectre.css/dist/spectre.min.css",
    "https://unpkg.com/spectre.css/dist/spectre-exp.min.css",
    "https://unpkg.com/spectre.css/dist/spectre-icons.min.css"],
  "dependencies": ["bionanoimaging/UC2-ImJoy-GIT:UC2_nip_demo"],
  "defaults": {"w": 20, "h": 10}
}
</config>
```

**JAVASCRIPT**

This handles the loading of the data, sending it to the processor and later visualization of the image:

```
<script lang="javascript">

class ImJoyPlugin {
  async setup() {
    api.log('initialized')
    // asuming you have a python plugin named "MinimalNIP", with a function named "getEngineURL" which returns api.ENGINE_URL, and another function "setParam1".
    const plugin = await api.getPlugin("UC2_nip_demo")
    const engine_url = await plugin.getEngineURL() // 'https://imjoy.pasteur.cloud'
    const fileInput = document.getElementById("file-input");
    // If user selected a new file or take a new photo, load it and do prediction.
    window.process = async ()=>{
      const file = fileInput.files[0]
      const upload_url = await api.requestUploadUrl({path: './test_.png', overwrite: true, engine: engine_url})
      const bodyFormData = new FormData();
      bodyFormData.append(
        "file",
        new Blob([file], {
          type: "application/octet-stream",
        })
      );
      await api.showMessage("Uploading a file to " + upload_url);
      await axios({
        method: "post",
        url: upload_url,
        data: bodyFormData,
        headers: { "Content-Type": "multipart/form-data" },
      })
      const param1 = document.getElementById("param1");
      await plugin.setParam1(param1.value)
      await plugin.process()
    }
  }

  async run(ctx) {

  }
}
```

### PROCESSING

The following code can be found in the processing file ```UC2_tools_janelia.imjoy.html```
**JSON**
This is the header managing the dependencies of the code. It automatically installs all the library in the miniconda environment to be able to use the Python code later:

```
<config lang="json">
{
    "name": "UC2_tools_janelia",
    "type": "native-python",
    "version": "0.1.0",
    "description": "[This is the backend to process any data which is coming from the cellphone.]",
    "tags": [],
    "ui": "",
    "cover": "",
    "inputs": null,
    "outputs": null,
    "flags": [],
    "icon": "extension",
    "api_version": "0.1.6",
    "env": "",
    "permissions": [],
    "requirements": ["numpy", "matplotlib", "pillow", "scikit-image", "scipy", "requests"],
    "dependencies": []
}
</config>
```

**PYTHON**

This code receives an image coming from a HTML-based Image Loader and process it e.g. edge detection. The final result gets sent back to the HTML GUI:

```
<script lang="python">
from imjoy import api
import numpy as np
from scipy import ndimage as ndi
from skimage.morphology import watershed
from skimage.feature import peak_local_max
from skimage import color
from skimage.filters import threshold_otsu
from skimage import morphology
from skimage.morphology import disk
from scipy import ndimage as ndi
from skimage import feature, measure
from PIL import Image
import base64

import matplotlib as mpl
mpl.use('Agg')
from matplotlib import pyplot as plt

plt.ioff()

class ImJoyPlugin():

    def setup(self):
        self.window = None
        api.log('initialized')

    def getEngineURL(self):
        return api.ENGINE_URL

    def setParam1(self, param):
        self.param1 = param

    def setURL(self, url):
        self.url = url

    async def process(self):
        await api.alert('processing with param1='+ str(self.param1))

        # Taken from http://opensciencecafe.org/2016/01/counting-change-image-analysis-python/
        # await api.alert('Processing the image')

        # load the image which was loaded through the GUI
        # await api.alert('Loading image from: '+self.url)
        myimage = np.array(Image.open(self.url)) #myimage = plt.imread()
        myimage_gray = color.rgb2gray(myimage)

        # Adaptive Thresholding the image
        thresh = threshold_otsu(myimage_gray, nbins=5)
        thresh_im = myimage_gray > thresh

        # Cleaning up the mask
        no_small = morphology.remove_small_objects(thresh_im, min_size=150)
        neurons = morphology.binary_closing(no_small,disk(3))

        # Masking
        myimage[neurons==False] = 0
        myimage_gray[neurons==False] = 0

        # Watershed Segmentation
        distance_im = ndi.distance_transform_edt(neurons)

        peaks_im = feature.peak_local_max(distance_im, indices=False)

        markers_im = measure.label(peaks_im)
        labelled_neurons = morphology.watershed(-distance_im, markers_im, mask=neurons)
        num_neurons = len(np.unique(labelled_neurons))-1  # subtract 1 b/c background is labelled 0
        await api.alert('number of neurons: %i' % num_neurons)

        # Plot the result and save as png in order to display it
        fig1, ax = plt.subplots(num='Labelled Neurons')
        plt.imshow(labelled_neurons,cmap='jet')
        name_plot = 'MyNeurons.png'
        plt.savefig(name_plot,dpi=300)
        with open(name_plot, 'rb') as f:
            data = f.read()
            result = base64.b64encode(data).decode('ascii')
            imgurl = 'data:image/png;base64,' + result
            data = {"src": imgurl}
            data_plot = {
                'name':'Plot charts: show png',
                'type':'imjoy/image',
                'w':16, 'h':20,
                'data':data}
        ## Check if window was defined
        if self.window is None:
            self.window = await api.createWindow(data_plot)
            print(f'Window created')
        else:
            print(f'Update window.')
            try:
                await self.window.run(data=data)
            except:
                self.window = await api.createWindow(data_plot)
                print(f'Could not print to old window. New window created.')
        await api.showMessage('done!')

    def imshow_overlay(im, mask, alpha=0.5, color='red', **kwargs):
        """Show semi-transparent red mask over an image"""
        mask = mask > 0
        mask = np.ma.masked_where(~mask, mask)        
        plt.imshow(im, **kwargs)
        plt.imshow(mask, alpha=alpha, cmap=ListedColormap([color]))

    def my_imshow(im, title=None, **kwargs):
        if 'cmap' not in kwargs:
            kwargs['cmap'] = 'gray'
        plt.figure()
        plt.imshow(im, interpolation='none', **kwargs)
        if title:
            plt.title(title)
        plt.axis('off')

    def run(self, ctx):
        print('Hello World')

api.export(ImJoyPlugin())
</script>

```

## TASKS

Exhange the part of ```# Watershed Segmentation```with an edge detection á la ```opencv``` canny-edge detection.

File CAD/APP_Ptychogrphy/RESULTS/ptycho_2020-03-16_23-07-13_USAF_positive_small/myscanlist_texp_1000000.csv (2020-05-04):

x | y
3.626700000000000159e+02 | 3.281299999999999955e+02
3.453999999999999773e+02 | 2.935899999999999750e+02
3.453999999999999773e+02 | 2.417800000000000011e+02
3.281299999999999955e+02 | 1.899699999999999989e+02
3.108600000000000136e+02 | 2.245099999999999909e+02
2.763199999999999932e+02 | 1.899699999999999989e+02
2.590500000000000114e+02 | 2.417800000000000011e+02
2.590500000000000114e+02 | 2.763199999999999932e+02
2.935899999999999750e+02 | 2.763199999999999932e+02
2.763199999999999932e+02 | 3.281299999999999955e+02
2.417800000000000011e+02 | 3.453999999999999773e+02
2.245099999999999909e+02 | 3.799399999999999977e+02
2.763199999999999932e+02 | 3.799399999999999977e+02
2.763199999999999932e+02 | 4.317500000000000000e+02
2.417800000000000011e+02 | 4.835600000000000023e+02
2.935899999999999750e+02 | 4.662899999999999636e+02
2.935899999999999750e+02 | 5.181000000000000227e+02
3.281299999999999955e+02 | 5.008299999999999841e+02
3.626700000000000159e+02 | 5.526399999999999864e+02
3.799399999999999977e+02 | 5.699099999999999682e+02
4.317500000000000000e+02 | 5.353700000000000045e+02
3.972099999999999795e+02 | 5.181000000000000227e+02
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

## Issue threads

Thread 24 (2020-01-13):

openUC2/UC2-GIT #24: How to rigidly mount camera in RaspiCam insert v2?

astraw, 2020-01-13:
Hi, I just printed all the files in `UC2-GIT/CAD/ASSEMBLY_CUBE_RaspiCam_v2/STL` but don't understand how the sensor is supposed to be held at a particular postion without play. Is there some way how the `20_Cube_Insert_RaspiCam.stl` part is held rigidly within the cube that I am missing?

Also, when I look closely at [this picture from the inline holography example](https://raw.githubusercontent.com/bionanoimaging/UC2-GIT/04edb5012f1e433878d4b0439712a9407a652075/CAD/APP_INLINE_HOLOGRAM/IMAGES/Application_Inline_Holographic_Microscopy_v2.png) (zoomed in and annotated below), it looks to me like the RaspiCam insert is rendered a few mm lower than is physically possible.  In particular, if you look at how the gray camera insert overlaps the dark green lid, it looks like the lid is occupying the same volume as the insert, which is physically impossible.

[image]

If I look at [the Camera Cube readme](https://github.com/bionanoimaging/UC2-GIT/blob/504b942e821c90b68e9c870a320eb38d880c2d3c/CAD/ASSEMBLY_CUBE_RaspiCam_v2/Readme.md) for help, this unfortunately does not clarify the situation for me. Also, the last image shows the sensor held by only a single screw, so perhaps a rigid mounting is not very important for this application.

beniroquai, 2020-01-16:
Hey! Thanks for reaching out! The photo you showed is indeed a bit misleading since the rendering indicates an error in the assembly. Once the components are printed it should fit. If you follow [this link](https://github.com/bionanoimaging/UC2-GIT/tree/master/CAD/ASSEMBLY_CUBE_RaspiCam_v2) you'll see how the camera module has to be assembled. The printed insert is "pushed" into the cube (e.g. press-fit or form-fit). You need a set of two screws to mount the Raspi-Camera. 

Is this somehow clear?

astraw, 2020-01-17:
Thanks for the reply.

The components do fit together, that is not the issue. Rather, the issue is that this is "too easy" -- there is substantial play of the insert within the cube. You say these are press-fit or form-fit but at least on my print, there is substantial play. This play is reduced when I insert screws into the cube and the threads of the screws touch the corners of the insert. For what it is worth, with this degree of play, I would not calibrate the camera as I think the camera would shift enough to give substantial error.

beniroquai, 2020-01-17:
Ah. This is interesting. May I ask you which printer you have? It's
supposed to be stiff and not very easy to move.
One thing we were thinking of is having a template to adjust the inner
component of each cube. Maybe we should have this for fixing them for long
time experiments. Please have a look here:
https://github.com/bionanoimaging/UC2-GIT/tree/master/CAD/EXT_Alignment_Tool

Best

astraw, 2020-01-17:
We have a Prusa i3 mk3. The template is a good idea for holding things more steady. I think I would just physically join the two pieces to be one piece at the 3D model level to hold it really steady.

Thanks again.

beniroquai, 2020-01-22:
So all good for now? :)

astraw, 2020-01-22:
Yes, thanks.

closed 2020-01-22 by astraw

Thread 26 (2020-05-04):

openUC2/UC2-GIT #26: Improvement of the TUTORIALS

b286, 2020-05-04:
We want to be user-friendly but to improve on that, we need users ;) 

Start with the UC2 project by following our [Tutorials of the TUTORIALS section](https://github.com/bionanoimaging/UC2-GIT/tree/master/TUTORIALS#-tutorials). Suggest improvements to the Tutorials if the instructions are not clear enough, more images are needed, something is not as obvious as we thought...

Mzyetik, 2022-05-27:
Tutorial-3 Lens Holder stl Files
STL file download options are not available on the links from the page https://github.com/openUC2/UC2-GIT/tree/master/CAD/ASSEMBLY_CUBE_Lens. For example , on the following link https://github.com/openUC2/UC2-GIT/blob/master/CAD/RAW/STL/20_Insert_Lens_holder_v3_-50mm.stl there is no download option.

beniroquai, 2022-05-30:
Hey @Mzyetik, thanks for reporting the error. We moved all STLs to this folder: https://github.com/openUC2/UC2-GIT/tree/master/CAD/RAW/STL

beniroquai, 2022-06-03:
Did you try hitting the `RAW` button? :-)

Alternative tools to access files easier through the browser are for example 
https://github1s.com/openUC2/UC2-Git

Mzyetik, 2022-06-03:
:D yes now I got there i got the directly the code to print as
[image] then but when I right click on RAW and save as, it let me to download, many thanks :)

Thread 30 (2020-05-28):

openUC2/UC2-GIT #30: Clarification of Baseplate connectors

AlecVercruysse, 2020-05-28:
Hello,

What is the purpose of the [Assembly_Base_Connector_4](https://github.com/bionanoimaging/UC2-GIT/blob/master/CAD/ASSEMBLY_Baseplate_v2/STL/Assembly_Base_Connector_4.stl)? Is it just the 4u version of [00_Connector_Baseplate](https://github.com/bionanoimaging/UC2-GIT/blob/master/CAD/ASSEMBLY_Baseplate_v2/STL/00_Connector_Baseplate.stl), meant for 3D designs? [The readme](https://github.com/bionanoimaging/UC2-GIT/tree/master/CAD/ASSEMBLY_Baseplate_v2) describes it as "length of 4 baseplate units" but nothing more.

 I am asking because, if I was constricted to a 120x120mm print bed, but wanted a 4x2 baseplate, I would need to connect two 2x2 prints. I know am able to construct the 2x2 base using [10_Base_v2](https://github.com/bionanoimaging/UC2-GIT/blob/master/CAD/ASSEMBLY_Baseplate_v2/STL/10_Base_v2.stl). Is the purpose of the holes along the x and y axes meant to facilitate the connection of these baseplates, with m3 screws and nuts?

Additionally, what is the naming scheme behind your CAD files, particularly the two digit number in front? 

Thank you for the help!

beniroquai, 2020-05-29:
Hey @AlecVercruysse, 

thanks for getting back to us! The Connector "Assembly_Base_Connector_4" is indeed an adapter to tilt the baseplate by 90° in order to build in the 3rd dimension. For concatenating base-plates you can conveniently print 2x2 plates and screw them together with M3 screws and/or mount them on a massive baseplate (i.e. Thorlabs optical tabels/breadboards, wooden plates, etc. ). Does this makes sense?

The naming convention - perhaps a bit confusing - is summarized in our [MDK](https://github.com/bionanoimaging/UC2-GIT/tree/master/MDK) with a detailed figure [here](https://github.com/bionanoimaging/UC2-GIT/raw/master/MDK/IMAGES/UC2-Module-Developer-Kit0.png).
We tried to differentiate between external and internal components.

AlecVercruysse, 2020-05-30:
This makes sense, thank you for the clarification!

AlecVercruysse, 2020-05-30:
This makes sense, thank you!

I see that 10_ corresponds to the "cube frame" components, 20_ to the cube inserts, and 00_ to any external parts, but I do not see in the figure the meaning of items labeled with 40_.

Particularly, in your [flex z-stage](https://github.com/bionanoimaging/UC2-GIT/tree/master/CAD/ASSEMBLY_CUBE_Z-STAGE_v2/STL), how does the `40_XY_Stage_Clamp_Slide_9.stl`  fit into this scheme? It seems like the rest of the hardware that clamps the slide is labeled with `30`, which makes sense as it can be considered "external module" hardware.

beniroquai, 2020-05-31:
Well, thats a very good question 😊 
It might be possible, that this is due to a wrong naming convention. Sometimes things are lost in chaos. The best would be to have some kind of online-configuator which outputs all files necessary for one setup as done in the [openflexure](https://ofm-stl-selector.netlify.app/#/v6.1.2?enable_smart_brim=true&reflection_illumination=false&optics=rms_f50d13&camera=picamera_2&use_pilens_optics_module=false&pi_in_base=true&base=bucket&riser=sample&include_actuator_drilling_jig=false&motorised=true&use_motor_gears_for_hand_actuation=false)

AlecVercruysse, 2020-06-02:
Such a tool would indeed be helpful in the future. Thanks, I'll close this issue since I understand the baseplate clarification.

closed 2020-06-02 by AlecVercruysse

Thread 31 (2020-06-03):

openUC2/UC2-GIT #31: Finishing MiniBOX

b286, 2020-06-03:
- [ ] eyepiece: yes or no? 
- [ ] sample holder - old version or new one with screws+magnets? 
- [ ] amount of baseplates: planned 8, do we want to sandwich it? -> then 16 
- [ ] sample mounting in smartphone microscope: is it clear and okay now? 
- [ ] lens holder: does the new version work well, stays closed? 
- [ ] which spring length/diameter for the z-stage? 
- [ ] z-stage working well?

RainerHeintzmann, 2020-06-03:
Is there an idea, where we finally get a low-priced set of lenses from?
Best wishes,
  Rainer

beniroquai, 2020-06-06:
Is there a way to add a simple spectrometer with the exsiting parts?

beniroquai, 2020-06-09:
Some more thoughts:
```
### Documentation

- Clear separation of the theoretical and experimental part 
--> Maybe: ray path, experiment ("template"), theory and resolution (with expected result)
--> "The phenomenon is in the foreground"
- Amount of text is ok; do not overburden pupils, keep up the "play instinct". 
- Text: In ray optics, it is better to speak of a "model"; e.g. "Rye-optics uses a model in which light rays are represented as lines..." 
- initial foil showing and naming all parts in the box (miniBox) (á la packing slip)
- Lens specification: "converging lens", diverging lens, focal length
- introduce the variables (e.g. f'=focal length, F'=focal point, a'=screen width, etc... according to DIN, see Pedrotti)
- Illustrated instruction for assembling a cube is missing
- QR codes with reference to the website / YouTube link?
- "Template" and lens position do not match, therefore reality! =Documentation (critical?)

###  Parts

- Haptic feedback per click is very desirable (this is lost for the time being with injection moulding?); metal stop is missing
- How can we mark the parts and their optical characteristics (colored, impact stamp?, adhesive dots)
- The box needs appropriate tools (hexagon) 

### Experiments

- It would be desirable if we could also build a spectrometer with the box (grating + slit) - should be feasible, right?

beniroquai, 2020-06-09:
And some input from Christina:

In your instructions there are various didactic elements which - according to my suggestion - should be clearly distinguishable graphically to facilitate understanding.

 ## Theory section

- illustrations - partly with explanations - in the form of beam paths
the images should be labeled again individually (converging lens, diverging lens, Galilean telescope...), especially if there are several images on one sheet
- Definitions ("Focus...")
- Mnemonics ("A telescope is...")

## Experiments

- Test setups
- Task (instruction for action and observation) (sometimes)
- Questions such as "What does the image look like through the lens?"
- Solutions, e.g. "With the right lens at the right distance..."

 

The structure should be the same for all instructions. Whether first theory part or first experiment is a matter of opinion, we discussed this before. Terms have to be defined beforehand, but we have also had good experience in explaining the observed phenomena AFTER the experiment.

 
The experimental part should also be uniformly structured, e.g. in the form question - structure - task - evaluation. The evaluation can be e.g. a small calculation, a gap text or similar... . Resolution can also be included, or you can make a sample solution - the teachers are always happy about that - but it should then be separate from the student worksheet.

One more tip about the tasks. They usually consist of an instruction for action ("Change the distance...") and an observation instruction ("Observe the object through the lens"). The latter can also be formulated as a question ("What does the image through the lens look like?"). The more concretely both are formulated, the better. "Test the lenses", for example, is very unspecific because the task of action and observation is not defined. A good test is always to have non-specialists read over it.

b286, 2020-06-12:
Include eyepiece: [10×/20](https://de.aliexpress.com/item/32897739739.html?spm=a2g0x.search0306.3.10.55b33e3cqAk1OO&ws_ab_test=searchweb0_0,searchweb201602_0,searchweb201603_0,ppcSwitch_0&algo_pvid=d07eadd7-1b43-443e-9a26-70fe7014a047&algo_expid=d07eadd7-1b43-443e-9a26-70fe7014a047-4) - 10,40€ per piece

b286, 2020-06-15:
The final designs of baseplates must be symmetrical for stacking and magnet-comptible. 
There are 8 baseplates in the miniBOX (final amount)

b286, 2020-08-05:
* making the IM stuff compatible
* baseplate puzzles

beniroquai, 2020-08-05:
Instead of the eyepiece we should go for 2*40mm lenses to build a Ramsden Eyepiece:
[image]

Since the cubes will be easy to open this is a nice alternative.

beniroquai, 2020-08-05:
We want a flyer which has a minimum dimension of 20x12mm (wide side is more important!) 
We want to have a Buchschraube which binds it. Like this:
[image]

b286, 2020-08-05:
Lenses: 
* 2× 40mm - [Artikel 2120](https://optikbaukasten.de/)
* 1× 100mm - [Artikel 2004](https://optikbaukasten.de/)
*1× -50mm - [LC1259](https://www.thorlabs.com/thorproduct.cfm?partnumber=LC1259)

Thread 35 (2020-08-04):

openUC2/UC2-GIT #35: XY stage

scientistnobee, 2020-08-04:
After reading your paper, I ordered the XY stage from Aliexpress. Along with the stepper motor connectors it has extra electronics parts, which I believe or end stops. Could you please confirm what they are for. The flex ribbon cable seems a better value, so can we find a connector for this?

beniroquai, 2020-08-04:
Hey @scientistnobee thanks for reaching out! I appreciate your interest in the UC2 project. The xy-stage from aliexpress indeed has flex cables, but buying the correct adaptor is quiet cumbersome. I didn't finde one which fits and designing a customized PCB makes reproducing by people outside the electronic community a little bit more complicated. 
Indeed there are two end stop sensors which can be used to detect the final position. If you're keen to use that for a calibration I would love to see that! Right now we do that with a raspberry pi camera and track the movement of the stage with sub-pixel frame registration. that works quiet well.

scientistnobee, 2020-08-04:
Thanks for your prompt reply and confirming that they are end stops. Do you have any link or extra info on how to use them. It has four solder joints. The sub pixel frame seems interesting. 

Some questions on the stage. Can a single XY-stage can bare the weight of a slide? Also, do we really need an extra IC to control the stepper motors? I think current from an Arduino board IO's is sufficient, so adding diodes might be enough to drive these tiny steppers.  

I can design the PCB as its my hobby. May be some people will be interested in it. 

Thank you.

beniroquai, 2020-08-04:
Hey, I found [this](https://www.hackster.io/news/these-two-small-steppers-are-one-giant-leap-for-maker-kind-7a6b3599cfae) a good read. I digged into the Aliexpress djungle, but unforutenyl I didn't find any additional information. 
Microstep scanning is more experimental. you need a second raspi lens and do a retro imaing configuration. From there you can do image processing. It's a 1:1 imaging in the range of pixelsize. Hope that helps :)

scientistnobee, 2020-08-04:
I think I come across the same project in a different version. https://youtu.be/s-a9CgvyQM8

I don't know much about the microstrip scanning. I will read about it soon.

beniroquai, 2020-08-05:
That's brillant! Thanks for sharing! :)

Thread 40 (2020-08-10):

openUC2/UC2-GIT #40: UC2 needs a better way to hold objective lenses - with different threads

beniroquai, 2020-08-10:
Most cheap optics are with RMS threadings, but I guess we should make this somehow adaptable - at least the part which slides through the z-stage. @b286 do you have a good way of doing that? Maybe something in Thingiverse? 

Perhaps it should look more like this rather than a full radial hole? 
[image]

@b286 any idea?

RainerHeintzmann, 2020-08-10:
... by the way. We should somewhere have our own RMS Tap.

Ich habe gerade privat einige 6mm Stangen (Thorlabs compatible?) geordert.
Mal sehen ob die Magnetisch sind. Hab da so ne Idee ....

VG,
  Rainer

*******************************************************************
Rainer Heintzmann
Leibniz Institute of Photonic Technology, Albert-Einstein Str. 9, 07745
Jena, Germany
(preferred mail address)
Tel.: +49 (0) 3641 206 431 Fax.: +49 (0) 3641 206 139
Institute of Physical Chemistry, Friedrich-Schiller-Universität Jena,
Helmholtzweg 4, 07743 Jena, Germany
jenaphotonics®
Tel.: +49 (0) 3641 948 350

beniroquai, 2020-08-10:
What do you mean by tap? Could you provide any drawings?

Regarding the rails: we had something in our very first designs in 2017.

RainerHeintzmann, 2020-08-10:
Gewindeschneider

---------------------
Rainer Heintzmann
Institute of Physical Chemistry, Friedrich-Schiller-Universität Jena,
Helmholtzweg 4, 07743 Jena, Germany
Leibniz Institute of Photonic Technology, Albert-Einstein Str. 9, 07745 Jena,
Germany
Tel.: +49 (0) 3641 206 431
---------------------------------

b286, 2020-08-18:
So we should offer the options RMS / M25. Is there anything else commonly used?

beniroquai, 2020-08-18:
Yes. Mostly RMS and M25. Eventhough both have almost the same thread. Maybe
we could get inspired with the openflexure triangular mechanism for threads?

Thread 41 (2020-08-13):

openUC2/UC2-GIT #41: Allow to mount 50mm diameter lenses

RainerHeintzmann, 2020-08-13:
Many of the easily available lenses (e.g. form Ajax Scientific have 50 mm diameter. It would be useful to also be able to mount them. 
They just about fit in the standard cube, but a different mount would be needed. It is not so important to have to full size as a transmitting surface.
Can one make a design for a variable holder for big lenses?

In addition it may also be interesting to make a design for a holder that can even deal with 10 cm lenses at a large distance from the front cube, for example to build a telescope with a 10cm entrance lense.

beniroquai, 2020-08-13:
Sounds interesting. We could definitely make a lens holder for the big lenses.

Something like this:
[image]

Can you please add more information about the lens diameter and thickness? 
A generic 50mm lens holder can be found here:
[20_Lens_holder_DIA_50mm.stl.zip](https://github.com/bionanoimaging/UC2-GIT/files/5070951/20_Lens_holder_DIA_50mm.stl.zip)

Would you mind to provide a drawing for the in-front-of-the-lens idea? That would help to clarify it a bit.

RainerHeintzmann, 2020-08-14:
That's pretty good. A retainment ring, which has the same size as your aperture and is flat and squishy would be good.

beniroquai, 2020-08-17:
Certainly. Would you mind to print this and see if this works? If so, I'll
provide the retain ring. We need to come up with an adjusted design though.
What are the lenses thicknesses?

RainerHeintzmann, 2020-08-17:
Here are the approximate measures:
(Double convex),  diameter= 50 mm, d_center=4,9mm, d_side=1.9mm
(Double concave), dameter=49,0mm, d_center=, d_side=4,8mm
(Convex-Concave, diameter=48,6mm, d_center=3.1m
( Concave -Convex), diameter=48,4mm, d_center=3,8mm
(Plano-concave), diameter=49,2mm, d_center=4,5mm
(Plano-convex), diameter=49,1mm, d_center=4,7, d_side=2,3mm

beniroquai, 2020-08-24:
Please find the new version of the lens adapter here:
[20_Lens_holder_DIA_50mm.zip](https://github.com/bionanoimaging/UC2-GIT/files/5120546/20_Lens_holder_DIA_50mm.zip)

If printed correctly it looks like this:
[image]

@b286 do you think one can add this design to the Thingiverser?

b286, 2020-08-25:
Making it adaptable to the lens thickness? That shouldn't be difficult, I'll make the openSCAD design for it.

closed 2021-02-03 by b286

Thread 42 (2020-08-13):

openUC2/UC2-GIT #42: New puzzled Baseplate should ship with variable Holesize for different printers

beniroquai, 2020-08-13:
We should provide different holes for magnets to give people to adjust it according to their (non)-calibrated printers. Maybe a Thingiverse configurator could do the job - or just a list of different STLs. Since we reduce it to only one part rather than ```1x3```, ```2x5```, etc. we don't need to do that for all the baseplates.

b286, 2020-08-18:
I don't quite understand what you mean. 

We could have an openSCAD design of the baseplate and using the Thingiverse Customizer, one could change a single parameter (hole offset) to change the diameter of the holes for the magnets. 

However, this would require everyone who prints the baseplate to experimtn with this and find the optimal setting. If someone want just 8 baseplate units, they might find it easier to file the holes a bit. For a little number of part, I certainly would. 

But is this something you had in mind?

beniroquai, 2020-08-19:
That's exactly what I meant. The new baseplate has two parameters: whole
for the screw and the magnet. I guess this could be made adaptable. I had
to experiment quite a lot in order to make it fit perfectly.
Maybe worth a try? Don't know how much effort that means for translating it
to openSCAD.

Thanks! )

b286, 2020-08-19:
The effort to translate it to openSCAD is not such an issue. What I see as an issue is that every user who would print the baseplates would also have to experiment with the printing quite a lot. But if it simply doesn't work otherwise, then it's worth it.

beniroquai, 2020-08-24:
Hm. Maybe we should provide a print-template which has holes ranging from 4.8-5.2 in 0.1 mm steps. Users can print it and see how "precise" their printer do their job and then they can print the "real" one.  Something like[this](https://www.thingiverse.com/thing:242437)

This emphasizes the reproducibility aspect. 

For the base plate, the only parameters would be the hole-diameter for the screw (M5) and the magnets. Eventually also the dimension of one plate element which may differ and add up with combining multiple of them..

What do you think?

CC: @RainerHeintzmann @ranranking

RainerHeintzmann, 2020-08-25:
Sure. Sounds like a sensible approach. 
Best wishes,
Rainer

---------------------
Rainer Heintzmann
Institute of Physical Chemistry, Friedrich-Schiller-Universität Jena,
Helmholtzweg 4, 07743 Jena, Germany
Leibniz Institute of Photonic Technology, Albert-Einstein Str. 9, 07745 Jena,
Germany
Tel.: +49 (0) 3641 206 431
---------------------------------

b286, 2020-08-25:
UC2 printing template, sounds cool. 

Does it make sense then to consider more parts than just the baseplates?

ranranking, 2020-09-10:
About the template/resolution target stuff. I am thinking about, if it makes sense to use normal printer to calibrating their 3D printers. What i am saying, is try to create some of a template print with their own different 3D printers and kind of calibration target with thier normal paper printer. So can compare the difference of the printing quality. The thing i am not really clear is, if all the paper printer choose 300 dpi to print, how big tolerance will the printer bring onto the paper.

b286, 2020-09-10:
I've created a ciälibrating tool that works reliably, in my opinion :) It will go to github soon.

beniroquai, 2020-10-13:
Awesome! Thanks 😊

closed 2023-01-22 by beniroquai

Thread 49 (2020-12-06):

openUC2/UC2-GIT #49: Print Mechanical Z-stage without support or add supports?

dakoner, 2020-12-06:
This page:
https://github.com/bionanoimaging/UC2-GIT/tree/master/CAD/ASSEMBLY_CUBE_Z-STAGE_mechanical_v2
says the parts can all be printed without support.
I printed the focus linear bearing flexure:
https://github.com/bionanoimaging/UC2-GIT/blob/master/CAD/ASSEMBLY_CUBE_Z-STAGE_mechanical_v2/STL/Assembly_Cube_Z-Focus_Linearbearing_1x1_v4_20_focus_inlet_linearflexure_v4_7.stl

and while the piece prints OK without support in the default orientation, the print quality is a bit low (the long bridges have lots of extra squigglies).  I don't want to add support on the bridging flexures, since it would be tough to remove.  Is there a way to put some internal supports in that can be easily removed to improve those? 

BTW I'm using a Prusa MK3S with PETG, but I can also do ABS and PLA.

b286, 2020-12-07:
Hi, 

Thank you for your comment. We print this part with a 0,15 mm layer height with the Prusa MK3S, using various materials, and while there are some extra filament pieces where the printer prints 'in the air', this shouldn't have any effect on the performance of the part. 

If you feel like it'S needed, you can od support but removing it is not so easy and in my experience you risk breaking something that should stay in one piece.

Kirk3gaard, 2021-06-02:
Hi 

I am surprised how well this printed even though there are quite a few horizontal pieces that have to be printed in the air. 

Best regards 
Rasmus 

[image]

closed 2023-01-22 by beniroquai

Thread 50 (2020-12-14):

openUC2/UC2-GIT #50: Lens holder for optical objective lens?

jediknightnapoleon, 2020-12-14:
Hi,

Just discovered this project. It is really amazing! Could you please let me know if it's possible to use the spiral or fixed lens holder for tube objective lens?

Many thanks!

Jerry

b286, 2020-12-14:
Hi Jerry, 

Thank you for your support :) The spiral holder can be generally used for any round object, the important parameter is the diameter of your tube lens. The holder found [here](https://github.com/bionanoimaging/UC2-GIT/blob/master/CAD/ASSEMBLY_CUBE_Lens_v2/STL/20_Cube_Insert_Objective_Holder.stl) can hold it if the diameter is up to 38 mm or so. It is useful to have the lens mounted in a tube or a ring. 

The fixed holders (for [small](https://www.thingiverse.com/thing:4377691) and [big](https://www.thingiverse.com/thing:4580156) lenses) can be adjusted for any diameter up to 50 mm but you need to have a bare lens in them.

jediknightnapoleon, 2020-12-14:
> Hi Jerry,
>
> Thank you for your support :) The spiral holder can be generally used for any round object, the important parameter is the diameter of your tube lens. The holder found [...]

Thanks a lot! I see, so I guess it would be better if I design a small ring/tube separately to mount the tube lens and then put the assembly on the spiral holder? Does the custom tube have to have any special structure to fit the holder? Also how does the spiral holder hold the lens securely? Does it only hold the lens horizontally or can it hold the lens vertically too?

b286, 2020-12-14:
If you don't have the lens in any mount, I'd rather suggest to use the fixed holder. the spiral holder is good for example for [mounted Thorlabs lenses](https://www.thorlabs.com/newgrouppage9.cfm?objectgroup_id=6277&pn=LA1131-A-ML) but as you can see in [this picture](https://github.com/bionanoimaging/UC2-GIT/blob/master/CAD/ASSEMBLY_CUBE_Lens_v2/IMAGES/CUBE_LENSHOLDER_1.jpg), putting in a bare lens means neccesarily touching it, which brings the risk of fingerprints and grease on the surfaces. 

The spiral is strong enough to just hold the lens in position, no matter whether vertically or horizontally placed in the cube. However, it might break after some time.

jediknightnapoleon, 2020-12-14:
Thanks, sory I didn't make this clear. I meant the microscopy objective lens like in [here](https://www.thorlabs.com/newgrouppage9.cfm?objectgroup_id=1044)
Is it ok if I use lenses like those?

b286, 2020-12-14:
I see, I understood tube lens. A microscope objective can be just placed into the spiral. However, in this case, it wouldn't be that stable when the objective is held vertically. For such application you can try the [new insert](https://github.com/bionanoimaging/UC2-GIT/blob/master/CAD/ASSEMBLY_CUBE_Z-STAGE_v3/STL/20_IM_Cube_Insert_Lens_holder_RMS_63x.stl) that is so far tested for the [new Z-stage](https://github.com/bionanoimaging/UC2-GIT/tree/master/CAD/ASSEMBLY_CUBE_Z-STAGE_v3). Would that solve it?

jediknightnapoleon, 2020-12-14:
I see, thank you. This seems promising. I'm just wondering how does this new insert hold the lens? Is it press fit or does it just have a smaller diameter so that the lens can rest on the hole?

b286, 2020-12-14:
It is pres fit - a RMS thread fits in the triangular hole in the insert.

jediknightnapoleon, 2020-12-15:
Do you have a picture of it in real life? It's a bit hard for me to imagine how this works. Don't worry if you don't have one. I guess I can just print one and try to sit a lens on :)

beniroquai, 2020-12-15:
Hey, certainly. I have just updated the documentation [here](https://github.com/bionanoimaging/UC2-GIT/tree/master/CAD/ASSEMBLY_CUBE_Z-STAGE_v3).
Please reach out if this is confusing. 
As @b286 already mentioned, we will switch to a new v3 design very soon. But don'T worry, everything stays compatible and great :-P

closed 2023-01-22 by beniroquai

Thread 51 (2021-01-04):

openUC2/UC2-GIT #51: "Inner Cube" For parts which lack enough supporting material

beniroquai, 2021-01-04:
For parts like the AlliedVision camera, we should perhaps design inserts that are an inner cube rather than just a plate. This could help the part to not move around. 
What do you think @b286 ?

b286, 2021-01-04:
This would definitely improve the stability but also limit the alignment range. Personally I didn't have any trouble with the camera moving around but I did have to align it to a certain position. 

It would also increase the printing time of those inserts. 

We ca design something like this and try it out :)

beniroquai, 2021-01-07:
Hmh. The camera is not really stably mounted inside the cube. Perhaps this is better:
[image]

What do you think?
@ranranking

ranranking, 2021-01-07:
Can we maybe not use two walls here? Is it not good for cooling? I dont know if it will be better, have kind of inner post from the bottom of the camera plate to the 'roof', which direct contact with the four vertical pillar of the cube, and fix the plate.
Or just make the wall on top side as well and have a opening window, which can fix a 12v fan inside ^^

beniroquai, 2021-01-08:
Would you mind making a sketch or even a CAD drawing? ;)

beniroquai, 2021-01-09:
@ranranking made this:
[image]

It works very well. We should upgrade at least the camera insert with this. 
Can you please do that @ranranking ? replace the original version with yours and close this issue? Thanks!

ranranking, 2021-01-11:
I have saved the new version with camera in V3 folder with the name of Assembly_Cube_AlliedVision_Alvium_v3

closed 2021-01-11 by ranranking

beniroquai, 2021-01-11:
Cool! Thanks a lot :)

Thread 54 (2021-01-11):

openUC2/UC2-GIT #54: UC2 configurator issues

b286, 2021-01-11:
### General issues  
- [ ] Lenses: how shall we take into account that there are different holders for different lenses and that the user might need to create his own? 

### GitHub 
- [ ] for v3 I omitted the version from the name of the module, since renaming everything everywhere is a hassle and this will save time in the future. However, all the modules that existed in git with ‘_v2’ in their name now appeared extra in the configurator and their folders also appeared again in the git CAD folder, with the only file in them being the ‘config.json’. The ‘_v2’ options in the configurator contain the v3 inserts that correspond to the module but not the cube and lid
#### STLs 
- [ ] is it necessary for each part to end with _v3? The .ipts and hence the generated .stls for which it matters do have it in their name already
- [ ] The renaming is a very good solution, although except for changing the prefix from UC2_v3 to UC2 only and cutting off the suffix number that Inventor creates when generating the file, I don’t see much difference. The “main” file names (without the prefix and suffix number) were matched between the excel and RAW/STL folder. Wouldn’t it be then enough to just cut the suffix numbers?

### Excel sheet 
- [ ] there must be some confusion between the v2 and v3 version of the excel sheet. or did you use a different tab than v3?
- [ ] the configurator doesn’t take into account the amount of parts stated in the excel sheet - shall the multiple parts be added as extra lines? 
- [ ] by making all the OPT parts default, the user might get more STL files than he needs - the question is whether printing some redundant parts makes him unhappy or whether it makes him unhappy not to find the parts in the zip folder when he needs them. I can’t decide what’s better 

### Configurator (general) 
- [ ] it would be nice to have a ‘clear all’ option for the case when one added a lot off different modules and got lost in it

b286, 2021-01-11:
### APPLICATIONS:
- [ ] all the downloaded zip files of the applications are empty, the list of files in zip is also always empty
- [ ] when adding a module of choice to an application, list and folder are again empty
- [ ] The applications sometimes give a different list of modules - the first time I selected an application there was a certain list. In some cases, from the second time on, there was a difference in either the first or the last module in the list. 
- [ ] The short descriptions of the setups that show under the selected app are the ones for a ‘complete overview’ tab, not from the latest ‘v3’ tab of the excel sheet

- [ ] Abbe experiment: 
- missing: 14x baseplate puzzle, 5x lens
- extra: 1x Sample holder

- [ ] Double-slit: 
- missing: 4x baseplate puzzle
- extra: 1x Sample holder

- [ ] In-line hologram: 
- missing: 4x baseplate puzzle
- extra: 1x RasPi Camera

- [ ] Incubator Microscope: 
- missing: 5x baseplate puzzle, 1x Z-stage
- extra: 1x Mirror 45

- [ ] Incubator Microscope fluorescence: 
- strange list, the APP should be anyways either updated or fused into the other one. Plus there’s another fluorescent microscope now and it became confusing 

- [ ] Light sheet: 
- missing: 15x baseplate puzzle, 1x Cylindrical lens, 2x Objective lens
- extra: 1x S-stage

- [ ] Mach-Zehnder: 
- missing: 11x baseplate puzzle
- extra: 1x Beam splitter 

- [ ] Michelson: 
- missing: 7x baseplate puzzle
- extra: 1x kinematic mirror

- [ ] Simple projector: 
- missing: 3x baseplate puzzle, 1x lens, (1xflashlight)
- extra:  -

- [ ] Simple smartphone microscope: 
- I should split it and make two list - for the mechanical-only one and the one with electronics
- missing: 8x baseplate puzzle, 1x Z-stage
- extra: 1x Sample holder 

- [ ] Simple telescope: 
- missing: 8x baseplate puzzle, 4x Lens (it’s empty)
- extra:  -

- [ ] Smartphone microscope:
- missing: 8x baseplate puzzle, 1x Sample holder, 1x Z-stage, 2x empty cube
- extra: 1x mirror 45

- [ ] Spectrometer: 

- missing: 6x baseplate puzzle, 1x Objective lens
- extra: 1x Sample holder

b286, 2021-01-11:
### MODULES:

- [ ] Baseplate 
- Baseplate 4x4 appers in the ZIP list, after clicking ‘download’ a bar saying ‘fetching data from GitHub’ appears but then nothing happens, nothing downloads 

- Alvium Cam ✓

- [ ] Aperture circular 
- everything works according to the list, but it’s supposed to have 7 leaves and not just one - shall Il add them as extra lines to the excel sheet or can this be fixed by selecting the amount from the right column?

- [ ] Aperture rectangular
- same trouble with the amount of parts that are supposed to be there more than once 

- Cube base ✓
- Basler cam ✓
- Beam expander ✓
- Beam splitter ✓

- [ ] Dichroic beam splitter 
- same trouble with the amount of parts that are supposed to be there more than once

- Eyepiece ✓
- LED ✓
- LED matrix ✓

- [ ] Laser 
- same trouble with the amount of parts that are supposed to be there more than once

- [ ] Lens 
- same as the baseplate: appears in the ZIP list, after clicking ‘download’ a bar saying ‘fetching data from GitHub’ appears but then nothing happens, nothing downloads

- [ ] Lens cylindrical 
- only insert, no cube 

- [ ] Mirror 45 
- nothing appears in the list, empty folder downloads 

- Mirror kinematic ✓
- Mirror kinematic 45 ✓
- Raspi cam ✓
- S-stage ✓

- [ ] Sample holder 
- it’s actually the sample comb 

- Z-stage mechanical ✓

- [ ] Z-stage objective 
- same as the baseplate: appers in the ZIP list, after clicking ‘download’ a bar saying ‘fetching data from GitHub’ appears but then nothing happens, nothing downloads 

- [ ] Z-stage sample 
- same as the baseplate: appers in the ZIP list, after clicking ‘download’ a bar saying ‘fetching data from GitHub’ appears but then nothing happens, nothing downloads

- [ ] Z-stage v3 
- works but the organisation of the Z-stage names is different in v3 now 

- two or more modules that work properly on their own can be added to the same selection and downloaded together, there are the correct parts in the zip folder

beniroquai, 2021-01-12:
Closing it for now, since all issues have been resolved here [https://github.com/bionanoimaging/uc2-configurator/issues](https://github.com/bionanoimaging/uc2-configurator/issues)

closed 2021-01-12 by beniroquai

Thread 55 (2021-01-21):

openUC2/UC2-GIT #55: Adding Folder for Sample Preparation?

beniroquai, 2021-01-21:
Perhaps we could add a short list of recipes for sample preparation with images for those who have never dealt with this. 
@RainerHeintzmann you could give an example of preparing the flowers for example
@ranranking  @b286 - perhaps some cools stuff from your work? Cheek cells and fibers are nice samples too. 

What do you think?

darwinbandoy, 2021-01-29:
would be interested to contribute infectious disease (DxBox) module focusing on common diagnostics like fecalysis and maybe generate identification keys for common parasites in domestic animals ( my DVM background).

beniroquai, 2021-01-31:
Sounds great! I could simply "copy+paste" the immuno fluorescent stuff I did so far. But I think it would be great to have something for the "ordinary" hacker who tries a light sheet microscope for the first time. In best case we could have it as a recipe based on off-the-shelf components.

closed 2023-01-22 by beniroquai

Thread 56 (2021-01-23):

openUC2/UC2-GIT #56: Magnetic screw issue (needs further documentation and alternative sources)

darwinbandoy, 2021-01-23:
First I would like to express my gratitude for the team who made this modular microscopy possible.

I was inspired to purchase a 3d printed to build my raman microscope. I have my spectrophotometer prototyped using lego blocks and on my way 3D printing the microscope components.

I purchased stainless steel (M3-0.50 x 12mm) on Amazon and the biggest surprise is it is not magnetic. This might be a potential issue for future makers, so can we add a list of tested and suitable materials specification indicating they can be magnetized? I see in the site a link to a European source but it would be useful to detailed out specific metal characteristics and warning that some stainless steel and zinc coated screws cannot be magnetized effectively.

b286, 2021-01-25:
Dear @darwinbandoy , 

Thank you for your nice words and your interest in the project. 

I believe we say that the screws should be made of galvanized steel in (hopefully) all the parts lists that appear through the repository. Stainless steel is in deed not magnetic. However, your point is very good - this might be causing confusion and leave the makers thinking that "steel is a steel, how different could it be". I will add an explanation to the Resources and the relevant pages.

dakoner, 2021-01-29:
'galvanized' is the not the best term to use if  you  search for  magnetic screws on amazon.  it brings  up a  lot of  construction screws  as well as machine screws.  galvanization is a surface coating, instead I think you want to select the steel's material properties 

Amazon actually has a "Screw filter" https://www.amazon.com/s?k=steel+screw&ref=nb_sb_noss_1 where  you  can  select  "carbon steel" a nd  deselect "stainless  steel".
I ended up getting https://www.amazon.com/gp/product/B015A34BUQ

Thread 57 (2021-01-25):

openUC2/UC2-GIT #57: UC2_v3 release

b286, 2021-01-25:
When do we merge the v3 branch into master? What is left to be done before that? 

- [ ] We should keep a link to the pre-merge point of the repository history somewhere on sight, at least for some time, for people who might still be working with v2. 

- [ ] The video updates by @edabngl can be done after merging the branch 
- [ ]  The SIM+ISM documentation @ranranking What's the state?

Anything else?

beniroquai, 2021-01-25:
We can create a Tag or release to the current version as v2.1?

beniroquai, 2021-01-25:
@ranranking do you need help to move openSIM/ISM to the configurator? I think it needs some polisihing ;)

ranranking, 2021-01-25:
I will try to update the ISM and get a nice image for it as well, we can see if it need some polishing after my push

获取 Outlook for iOS<https://aka.ms/o0ukef>

b286, 2021-01-25:
- [ ] @b286  check and update the google spread sheet, hide confusing old information 

I think such a release wouldn't be that different from the last one. I'd suggest to put somewhere visibly in the main readme a link to the fixed point in the history of commits - the way we did it with the link in the Nature paper. That way it can be easily browed.

beniroquai, 2021-01-25:
You should see it here: 
[image]

Regarding ToDo's .. I'm waiting for the go from @ranranking then I'll review the UC2-configurator once again :)

ranranking, 2021-01-25:
I have pushed the new version of the  configurator excel, maybe you can have a look when you have time. I have upgraded the ISM module with the Z-Stage, STL and cover images are also in the folder they should be.

beniroquai, 2021-01-25:
Thanks @ranranking I checked the list. It compiles now, but there are issues with the parts it seems..

Also @b286 and @ranranking the following parts are still missing in the STL RAW folder: 
```
20_Insert_Large_Lens_holder_v3 is missing
30_LS_Sample_stage_v3 is missing
20_focus_inlet_linearflexure_motorized_small_v3 is missing
30_CUBE_openSIM_Lid_v3 is missing
```

Cover image for SIM is missing

beniroquai, 2021-01-25:
Looks good so far, except the ISM:

[image]

Intentially? 50 puzzle pieces? ;)

ranranking, 2021-01-25:
I added 50 pieces because i am not sure about how to configure it. I set 50 is for both openSIM and ISM togther, because in the tutorial i wrote all based on the setup combined togther but on the figure is separate. Should just write as on the example figure?

beniroquai, 2021-01-26:
That's fine; We need to decide if we really want to include all modules in the setup, but since the `APP_openSIM/ISM` is a fully assembled setup, it should have all the modules. Would you mind adding the other components too? I think you can copy/paste the entries from openSIM. 

Also once again, the spelling must (!) be the very same as the actual files ;-)

b286, 2021-01-26:
I know what the release looks like, but then you can just download it as a zip file. Considering the comfort of, for example, my currect high school pupils I think the option to browse through the page normally is more convenient. 

Missing files added. All files are (fingers crossed) the latest version.

beniroquai, 2021-01-27:
So then let'S create a new v2 branch derived from the last master before merging to v3?

beniroquai, 2021-01-27:
The latest commit looks good, no missing `STLS` any more thank you! 👍

beniroquai, 2021-01-27:
Also; The openSIM and openISM Application was still wrong, something was bad with the numbers..all shifted. Corrected it.

b286, 2021-01-28:
v2 branch, that's a neat solution! Thanks for the idea, I'll do that.

b286, 2021-02-03:
Anything missing or are we ready? 

Videos by @edabngl are almost all published now. 

If the SIM and ISM parts are done, I'd pull it into master this week.

edabngl, 2021-02-03:
Yes. I uploaded 6 new YB videos for v3 cubes and baseplates.

beniroquai, 2021-02-03:
I like what I see! Very much indeed! :) 
Well done @b286 and @edabngl!! 
I checked the configurator once more, everything looks good to me. Certainly there are some issues in the github, I'll try to sort these out soon! :)

You have my blessing :p

beniroquai, 2021-02-03:
@b286 perhaps we should think about a "launch campaign" like [this one](https://twitter.com/OpenFlexure/status/1356632596172668934) ;-)

b286, 2021-02-04:
Totally. You mean something big scale?

beniroquai, 2021-02-04:
Well, you had this funny idea of filming someone assembling an ordinary cube and our injection moulded stuff with a stop-watch in the background. Something like that. Could be "BIG" wrt. new version 3.

b286, 2021-02-05:
Yes, we'll film this with Eda once I can come to work. Shall we then wait with the release a use this video to advertise it?

beniroquai, 2021-02-06:
Yes! Let's summarize the advantages of v3 in a twitter thread like the one from [openflexure](https://twitter.com/OpenFlexure/status/1356632596172668934)

closed 2021-03-19 by b286

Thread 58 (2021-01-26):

openUC2/UC2-GIT #58: Spectrophotometer alignment

darwinbandoy, 2021-01-26:
I am working on a raman microscope, one of the components is a spectrophotometer.

I decided to follow the current working guide but doing so will not generate any spectra.

The camera or imaging module must be perpendicular to the diffraction grating. 

In my case I placed a perpendicular 45 degree mirror so spectral image is reflected on top where a phone or webcam imager can be conveniently placed.

beniroquai, 2021-01-26:
Hey @darwinbandoy, thanks for filing this issue. Do you want to directly use the [UC2 Spectrometer](https://github.com/bionanoimaging/UC2-GIT/tree/master/APPLICATIONS/APP_Spectrometer) for Raman imaging? This sounds tough, but I'm sure you have adapted your design already or? 
@edabngl has made some experiments with the spectrometer, perhaps she can help you?

darwinbandoy, 2021-01-26:
I made multiple modifications: 

1) I created covers but PLA is too shiny so I added black paper to reduce reflection
2) I controlled light entry by coupling fiber optic as entry point
3) I designed a diffraction grating mount 
4) I modified the alignment of the diffraction grating with mirror and imaging system 

I am still doing some modifications but I can share my modified version if this valuable to the community. 

Would love to reach out to other makers out there.

beniroquai, 2021-01-27:
It would be brilliant to see that! I'm very curious. Would you mind sharing it here? 
Also if you want you can contribute with a pull request. 
We will ship the version "v3" in the next days. Everything will be compatible though, don't wonder ;-)

darwinbandoy, 2021-01-29:
So far the fiber optic spectrophotometer prototype is working (generates spectra). 

I will do some refinements and would share the results here.

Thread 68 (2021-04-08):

openUC2/UC2-GIT #68: z stage for samples

jediknightnapoleon, 2021-04-08:
Hi,

I'm just wondering how does the z stage for samples hold the sample (for example a slide)? Do we just loosely put the slide on top of the translating stage? Also is it possible to just use a screw instead of a motor to adjust the height of sample manually like in the z stage for objective?

Many thanks,

Jerry

ranranking, 2021-04-08:
Hallo Jerry,

thanks for using the UC2 modules.

We have a new version of z stage, which moves the height of the sample instead of move the objective.
https://github.com/bionanoimaging/UC2-GIT/blob/v3/CAD/ASSEMBLY_CUBE_Z-STAGE_sample/STL/20_Cube_Insert_Z-Focus_single_v3.stl
It is designed for using a micrometre to fine adjusting the z position of the sample. You can get more information here:
https://github.com/bionanoimaging/UC2-GIT/tree/v3/CAD/ASSEMBLY_CUBE_Z-STAGE_sample

I hope it solves your problem and feel free to come back to us again.

Cheers,
Haoran

beniroquai, 2021-04-08:
Indeed, the Z-stage is a critical topic ;-) 
Always open for suggestions! In fact, the stage can be used for moving the objective as well as the sample. How do you like to work with it? Perhaps we can adapt it to make it more useful?

jediknightnapoleon, 2021-04-09:
Hi both,

Thank you very much for your replies! I see, could you please advise on how to assemble the z stage with a micrometer as the z controller? On the z stage cube page it only shows how to assemble with a motor so I'm not fully sure how a micrometer can be inserted. 

Could you please also recommend any specific micrometers that fit this version of z stage? 

Many thanks,

Jerry

beniroquai, 2021-04-17:
Hey, thanks for the remark. Indeed the Z-stage using the micrometer doesn't seem to be very well documented. 
We use micrometers from [RS Electronics](https://uk.rs-online.com/web/p/micrometers/7857878/).. @ranranking would you mind to add some images from your z-stage with the micrometer and the link to the RS parts please? :)

ranranking, 2021-04-21:
Hallo,

Here is a picture of the z stage with micrometre, the micrometer is fixed with screws from 3 sides and the rubber band can provide the backlash. 
[image]
It's better to use the similar micrometre as on the picture with a flat front surface on the rod, otherwise it will have a step leap after every turninig cycle.
An example is showing here
https://github.com/bionanoimaging/UC2-GIT/blob/v3/CAD/ASSEMBLY_CUBE_Z-STAGE_sample/IMAGES/Zstage.jpeg

jediknightnapoleon, 2021-06-02:
Hi would it be possible to just use a screw to move the z stage? I seem to remember there was a previous version which just use a long M3 screw but I'm not sure how it works exactly.

b286, 2021-06-02:
Hey, 
There is still the [mechanical Z-stage](https://github.com/bionanoimaging/UC2-GIT/tree/master/CAD/ASSEMBLY_CUBE_Z-STAGE_mechanical) that just uses a wheel on a long M3 screw. Other than that, I don't know which version do you have in mind.

jediknightnapoleon, 2021-06-02:
Hi,

Thanks for your reply. I tried the mechanical Z-stage you mentioned but had to modify the objective holder to fit my Olympus RMS20X objective. Unfortunately as this is bigger than yours the weight of the objective seems to cause the objective-holder complex to rotate around the screw and point slightly downwards. Is there any way I can fix this misalignment?

Many thanks!

b286, 2021-06-09:
Hi, 

I'm afraid we don't have a solution for this at hand, as we never used the mechanical stage for a real microscopy application, but rather for education with the small objective. However, we are currently working on a new, improved, and "stronger" objective stage, so a solution is hopefully coming soon.

beniroquai, 2021-06-09:
May I ask you to take a picture from your z-stage? PErhaps we have alternatives ;-)

jediknightnapoleon, 2021-06-14:
Hi all,

Thank you for your replies and sorry for the delay. I have attached two photos of my current cube for the objective. It basically uses the mechanical z stage but I modified the objective holder. It now holds the lens but if I try to adjust the position (e.g. translate the lens for focusing) of the objective then the orientation of the objective changes too because there is large friction between the holder and the 'fence'.
[image]
[image]

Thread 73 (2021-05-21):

openUC2/UC2-GIT #73: Questions about Lenses and the Beam Splitter

Zmrf, 2021-05-21:
Hello,
I've got 3 Questions regarding the Fluorescence Microscope (infinity):

1. In "Parts" it says "Tube lense according to objective lens", what kind of lens is needed for an 10x objective?
2. The Laser, the Beam Splitter and the Emission Filter need to be choosen specific for the used Fluorescence Protein, right? 
3.  If yes, what Kind of Beam Splitter ist needed for TurboGFP with Excitation max at 482 nm and Emission max at 502 nm?

Greetings
Darius

beniroquai, 2021-06-04:
Hey Darius, 

many apologies for the late repyl! 

In order to answer your questions: 

```1. In "Parts" it says "Tube lense according to objective lens", what kind of lens is needed for an 10x objective?```

The tube lens in combination with the objective lens determine the full magnification of your optical system. For Zeiss, the tubelens length is 165, for Nikon/Olympos 200mm for example (not always though). If you grab an infinity corrected lens form Aliexpress or alike I would calculate with either 180mm or 200mm if it's not specified. More information are to be found [here](https://www.microscopyu.com/tutorials/offaxisrays). 

```The Laser, the Beam Splitter and the Emission Filter need to be choosen specific for the used Fluorescence Protein, right?```
Yes, exactly. If you want to have a filter cube for GFP for example, you excite the sample with 450nm Laser (blue), the protein fluoresces in green (e.g. 500nm) and this signal you want to detect on a camera. So you would need a system that reflects the blue, but does transmit the green. You can find more information on our [github page](https://github.com/bionanoimaging/UC2-GIT/blob/88be02412cd414ffad5aac8310d01578f0929374/CAD/ASSEMBLY_CUBE_Dichroic_Beamsplitter/Readme.md) and also from the people from the openflexure community [here](https://gitlab.com/openflexure/openflexure-microscope/-/issues/131), [here](https://github.com/rwb27/openflexure_microscope/issues/43) and [here](https://www.osapublishing.org/boe/fulltext.cfm?uri=boe-11-5-2447&id=429869) (also for GFP if I remember correctly). 
Let us know if you have more specific demands. We usually work with synthetic dyes (e.g. Alexa Fluor).

```If yes, what Kind of Beam Splitter ist needed for TurboGFP with Excitation max at 482 nm and Emission max at 502 nm?```

I guess so. 

Greetings

Zmrf, 2021-06-16:
Thanks for ur Answer.

Greetings :)

closed 2021-06-16 by Zmrf

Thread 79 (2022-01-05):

openUC2/UC2-GIT #79: PSRAM ID read error - ESP32 while flashing LED matrix code

dhersm, 2022-01-05:
[image]

Can't connect LED matrix with the ESP32 for the Incubator microscope. While checking the serial monitor, it shows the error in the picture given.

errors:
PSRAM ID read error: 0xffffffff

abort() was called at PC 0x40089631 on core 1

beniroquai, 2022-01-06:
That is hard to debug. Did you enter the correct settings in the ESP32 Arduino IDE tool? Did you activate the PSRAM? 
Could you check just uploading the LED Matrix example from Adafruit?

dhersm, 2022-01-07:
Yes ,  the settings are correct. As you suggested, we enabled PSRAM and the PSRAM error is solved but "abort() was called at PC 0x40086ed5 on core 1"  is still there. The motor is connected successfully via MQTT but the LED array is not.

beniroquai, 2022-03-03:
I hope the error was resolved finally.

closed 2022-03-03 by beniroquai

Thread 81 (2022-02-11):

openUC2/UC2-GIT #81: Motorised polarizer/filter rotating stage

GiuseppeCiccone96, 2022-02-11:
Hi,

I think it would be really nice to integrate a motorised polariser/filter mount that is compatible with the uc2 framework and easily adaptable to other open-source microscopy projects such as the OpenFlexure.
A starting point can be [This paper](https://opg.optica.org/ao/fulltext.cfm?uri=ao-60-13-3764&id=450413), where they present a step-by-step guide to 3d print and assemble motorised rotating mounts for both transmission and reflection configurations!

beniroquai, 2022-02-14:
Hey Giuseppe, 

thanks for pointing to this nice paper. I would really like to see this functionality in our system. Also it could help reducing speckles. 
I did a quick mockup using 3 ball bearings, a 3D printed timing belt and a 28byi stepper motor. What do you think?
[image]

GiuseppeCiccone96, 2022-02-14:
Hi Bene,

thanks so much for the quick try! 

I think it looks very promising - perhaps it could be integrated into the "APPLICATIONS" repository with instructions? 
Maybe one example could be an illuminator for polarization microscopy (I would like to try this out but we are currently moving labs and I don't have access to any equipment).

Thanks a lot for your support :) 

Giuseppe

beniroquai, 2022-02-16:
[Tadah](https://github.com/openUC2/UC2-Motorized-Rotator). 
[image]

Feel free to comment :-)

closed 2022-02-16 by beniroquai

GiuseppeCiccone96, 2022-02-16:
Hi Bene, looks fantastic! 

I think the link may be broken though?

Giuseppe

beniroquai, 2022-02-16:
Fixed. Sorry, for some reason it was set to private :)

GiuseppeCiccone96, 2022-02-16:
not sure why but it still gives me error 404... :(

beniroquai, 2022-02-16:
Hey, I'm very sorry. Now its really public!! ;-)

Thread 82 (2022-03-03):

openUC2/UC2-GIT #82: UC2 injection moulded cube optimization thread

beniroquai, 2022-03-03:
I wanted to take the chance to collect some feedback in order to improve the injection moulded cubes. Please feel free to add whatever comment so that we will have a refined version that is less harmful, yet compatible and long lasting. 

I wanted to talk about this cube/baseplates
[image]

@edabngl, @b286, @renerichter, @ranranking

Some points I would like to revise:

- [ ] Sharp edges cause pain when pressing parts together or simply may cut the skin
- [ ] Where to place potential electronics?
- [ ] Sysytem is mechanically overconstrained 
- [ ] The inserts can never be "straight" since there is no kinematic mounting possible
- [ ] The current cube is not 3D printer friendly (e.g. the pins are not M5 or alike)

**Further important question:**
Do we want to keep the standard persistent or do we want to introduce a new formfactor?

I'm very open for any kind of discussion! Thank you!

beniroquai, 2022-03-06:
In order to get the cube "straight", perhaps we could think about a mix of the Thorlabs rails and the mysterious railoptics:
[image]

I could imagine having a modified version of an insert or even some extra hack at the cube's edges? 

Or even a modified thingy from the caliper. It's quite accurate to work with it

[image]

RainerHeintzmann, 2022-03-06:
That's not a bad idea. Let's talk about it.

beniroquai, 2022-03-06:
Sure!

One more thing to add: baseplates should be compatible with laser cutting
manufacturing.

ranranking, 2022-03-07:
I'd like to have some lock mechanism, it helps a lot to hold the optics position. Is that possible to have a small groove at cube parts connection that can open the cube easily without threaten the optics?

beniroquai, 2022-03-07:
One more "thing": make magnet-based and stackable option compatible by adapted baseplate, but same IM cube:

- have the holes for the pins in the baseplate bigger so that no force is required to put them together
- laser-cut parts could be used for magnet-based version? 3 layers, then magnets are "fixed" forever? (e.g. Sandwich)

beniroquai, 2022-03-07:
And: "expansion mechanism" for fixing the insert permanently.

beniroquai, 2022-03-08:
@ranranking do you mean a lock mechanism to not accidentally open the cube`? Definitely Important!

beniroquai, 2022-03-16:
One more thing I really don't like is that the baseplates are sometimes sticking together too stiff. Also the cubes are residing on the baseplate so that one cannot get them out easily. Sometimes the pins are too big for the holes which causes an additional distance between plate and cube. 

One more thing is the positive/negative wings of the puzzle piece. Sometimes they are "in the way". Solution would be a pure "female" and "male" version of the baseplate?

Kubiczek36, 2022-03-20:
Hey,

I like the simple way the cubes are. Maybe I would think about modifying the inserts. Here I got some suggestions.

[image]
[image]

And as i understood it right. You are aiming to produce the baseplates on laser cutter (for example from PMMA). And there would be software to generate the files for the cutter based on which layout you like to use. Then I think could be nice to make _two-story architecture_ with zero floor for electronics, stretch the cables through the holes in the baseplate to control the _optics floor_.
[image]

beniroquai, 2022-03-20:
That looks great! We should have a hackathon for brainstorming a bit! 
For locking I though a bit simpler. Similar to these "guys":
[image]

Having a flexure bearing that is squeezed and then locked in place of the cub - and potentially even straightens the insert. 

Electronics is a whole different thing. So far we collect some ideas [here](https://github.com/openUC2/UC2_Feather). This is cube-contained + a baseplate connector, but this is just a mock-up.  I did not fully get your mechanism yet. Night to play with the doodle.

RainerHeintzmann, 2022-03-21:
"Similar to" could possibly mean "use these guys"?

beniroquai, 2022-04-08:
We should also think about having an insert inside an insert, so that we can injection mould the global insert in order to have higher precision + better reproducibility. + the global insert should have a locking mechanism

beniroquai, 2022-04-08:
Having more holes for adding shielding plates is also mandatory

beniroquai, 2022-04-21:
The "Masterinsert" should have press-inserts for screws. Perhaps M3. PErhaps ferromagnetic?

beniroquai, 2023-09-29:
- Wechseleinsätze um Noppen rasuzunehmen
- Löcher an Seite genauso groß wie Puzzle (34mm)
-

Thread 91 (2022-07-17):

openUC2/UC2-GIT #91: About Fluorescence Microscope (infinity)

Mzyetik, 2022-07-17:
Dear All,

Some of the component links dont work (especially this one 1x Objective lens, No Name, 100x, NA1.25, 50 Euro, China ) in the Infinity Florescence Microscope page:

https://github.com/openUC2/UC2-GIT/tree/v3/APPLICATIONS/APP_Fluorescence_Microscope_infinity

We would be happy if it could be updated.

Besides, here we wonder about the objective lens. In this Florescence Microscope, do we need a special objective florescence lens? (which 10 times around more expensive). Or are the non-florescence objective lenses currently suggested proper also for florescence?
We highly appreciate your answer in case we may buy directly a florescence objective lens instead a normal one.

many thanks

beniroquai, 2022-07-19:
Hey, thanks for reaching out. 
In general the quality of the objective lens is determined by its name (e.g. apochromat). Fluo usually means that you have additional antireflection coating. Additional information is nicely summarized here https://www.microscopyu.com/microscopy-basics/introduction-to-microscope-objectives

Decent lenses for relatively low pice are available from Nikon and Bolioptics
e.g. https://www.bioform.de/shop.php?action=tree&wg=2&pid=5107&treeid=5308
and https://bolioptics.com/microscope-parts-accessories/objective/infinite/

Looking forward to your PR :)

Mzyetik, 2022-07-19:
Thank you also for your kind answer about Fluorescence 

How about achieving phase contrast in your setup? Do they need special objectives as we are used to?

many thanks

beniroquai, 2022-07-20:
Hey, you can use oblique illumination or darkfield. The alternative would
be purchasing a phase-contrast objective and use a ring illumination.

> Message ID: ***@***.***>
>

Mzyetik, 2022-07-26:
Many thanks for your kind answers, I hope we can mount it on UC2 microscope setups, by the way how to print focus_inlet_linearflexure https://github.com/openUC2/UC2-GIT/blob/master/CAD/RAW/STL/20_focus_inlet_linearflexure_v2-3_1x1_v3.stl 
[image]
we were not successful although did several trials , especially the support is not removable , we would be happy for your kind advice.

beniroquai, 2022-07-26:
Hey @Myzetik, 

thanks for your message. In fact, this stage is already fairly old and I cannot support this design anymore. We moved to NEMA stepper motors in our recent results. 
If you send a photo, perhaps I can tell what could be improved ;)

Mzyetik, 2022-07-27:
Thank you very much for your answer, and informing about the new version. I checked it as well https://github.com/openUC2/UC2-GIT/blob/v3/CAD/RAW/STL/UC2_20_Cube_Insert_Z-Focus_single_motorized_v3.stl regardless of new or old version, the 3D printer requires to use support to print these nicely designed structures but then it is not possible to remove the support as seen the one on the picture.
[image]
We are so curious how could they be printed (what is the trick to manage it with normal PLA printers, here we use Ultimaker 2+ . Many thanks for your support and patience :)

beniroquai, 2022-07-28:
Did you try printing without the support? Not sure if @b286 has any insights here ;)

wbrett87, 2022-08-15:
Hi, if you havn't resolved this issue yet:

1) Flip it over in your slicer software so the largest area touches the printing bed. 
2) Print WITHOUT support - this is what helped the most for me. Your printer should be able to "bridge" this distance.

beniroquai, 2022-08-15:
Thanks!:)
In general: if you use the full prusa ecosystem including their filament and slicer, chances of a successfully printed microscope are very high. :)

wbrett87, 2022-08-16:
I used a Creality 3 ender pro with good results

beniroquai, 2022-08-16:
Which settings and Filament if I may ask you?

wbrett87, 2022-08-16:
I used Inland blue PLA(from Microcenter here in US).  It needs hotter temps than your average PLA but once I figured that out it worked great. I can't remember the settings offhand but I will put them here when I get home from work. I used the Ultimaker Cura slicer.

Mzyetik, 2022-08-16:
> 

Thanks a lot, some of our friend used water soluble support material but it resulted with a warped holder, then the better solution is your suggestion we will try it, thank you again for the continuing discussion, it is quite informative

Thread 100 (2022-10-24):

openUC2/UC2-GIT #100: Incomplete parts list for Polar BOX

b2jia, 2022-10-24:
Really interested in building up a PolarBOX for self-learning! I noticed that 

1. many of the links on [the parts list](https://github.com/openUC2/UC2-GIT/tree/master/TheBOX/PolarBOX) are either broken or missing (ie. which mirrors? which circular polarizers?)
2. the 3D parts are not on [UC2-configurator](https://uc2configurator.netlify.app/), is there a reason? 
3. assembly links are broken

Thanks in advance!

edabngl, 2022-10-24:
Hi. Actually, all STL files are included specifically in each application page, STL folders. But I recognised now that Build_Me page links need update, thank for feedback.

Just follow [this page ](https://github.com/openUC2/UC2-GIT/tree/master/TheBOX/PolarBOX)  and the application page links for STL fıles. Unfortunately, we don't have ready-to-download file for all necessary 3d printed parts but will add it in the following period. And the broken links will be fixed.

beniroquai, 2022-10-24:
@edabngl are you keen on fixing the links? ;-)

beniroquai, 2022-10-24:
I quickly implemented a URL-checker in github actions: https://github.com/openUC2/UC2-GIT/actions/runs/3312545528
I fear there are many dead links :-/

edabngl, 2022-10-24:
@beniroquai I can organize the folder, deletes unnecessary parts and add the links to already organized pages. But not this week, maybe next week :)

beniroquai, 2022-10-24:
Cool :)

Here is the summary:
https://github.com/openUC2/UC2-GIT/actions/runs/3312545528/jobs/5469341816

Look for "dead links" ;-)

b2jia, 2022-10-24:
Thanks both for your support. I want to clarify one thing - it looks like a few of the non 3-D printing parts are not listed (ie. mirrors, birefringent material, circular polarizers). Is there a parts list for these as well?

edabngl, 2022-11-17:
Hi @b2jia . I updated [BUILD_ME](https://github.com/openUC2/UC2-GIT/tree/master/TheBOX/PolarBOX/BUILD_ME) page of PolarBOX, broken links and missing images and links were added. If you can't find the details of the module in BUILD_ME, please go to directly the Application page for more details i. e. [Circular Polarization](https://github.com/openUC2/UC2-GIT/tree/master/APPLICATIONS/APP_POL_Circular_Polarizer) for the details of the circular polarizers and [Stress Birefringence Experiment](https://github.com/openUC2/UC2-GIT/tree/master/APPLICATIONS/APP_POL_Stress_Birefringence) for birefringent sample alternatives which I used there.

closed 2022-11-17 by edabngl

beniroquai, 2022-11-18:
@edabngl @b2jia please find the newly organized documtation for the polarbox here: https://openuc2.github.io/docs/DiscoveryKit/Polarisation/APP_POL_Brewster_Angle_Experiment/

CC: @renerichter @ranranking

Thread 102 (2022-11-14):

openUC2/UC2-GIT #102: Circular aperture leaf too thin to print

b2jia, 2022-11-14:
Regarding `20_Cube_Insert_CirAp_Leaf_v3.stl` as requirement for the light sheet microscope, it looks like the thickness of the leaf is only 0.3mm. We have tried printing this many times to no avail. We are wondering (1) is this truly the correct thickness? (2) can it be "thicker" to work, or is the tolerance extremely small?

[image]

beniroquai, 2022-11-14:
Dear @b2jia many thanks for your message. Unfortunately, the person who developed it (@b286) no longer supports this module. Perhaps @edabngl, can you help out here? :)

b2jia, 2022-11-14:
@beniroquai thanks for your response! Just checking it is permissible to increase the thickness of this aperture leaf. I checked the clearance on the aperture wheel (onto which the hole in the leaf locks in), it's 0.6 mm in thickness. I'm thinking of both increasing the extrusion on the aperture wheel (0.6mm -> 1 mm), and the thickness of the leaf (0.3 mm -> 0.7mm).

edabngl, 2022-11-15:
Hi @b2jia , I used this design before, and I got problems with assembling the leaves to the wheel. So, my solution was the updating the wheel holder part with edges which is an up-to-date design for now. 
If you change the edge design, which you mentioned as 0.6mm -> 1 mm  (I marked this part in the image), I think you can use thicker leaves in the design. There is enough gap between the lid and guide parts for the changes. I hope it works well :)

[image]

closed 2022-11-15 by edabngl

b2jia, 2022-11-24:
For future posterity: in case others are also trying to print this aperture, 

- increasing the leaf thickness to 0.6 mm was sufficient
- increasing the clearance on the wheel (circled above) to 1 mm was also sufficient
- the clips on the wheels needed to be filed down in order for the leaves to hook on
- for future note: print the leaves with a non-transparent material (white shown below; partially translucent)

https://user-images.githubusercontent.com/37123556/203666007-abb8c5c7-1da0-4c9d-acfb-e5fa386cf78c.MOV

beniroquai, 2022-12-05:
@b2jia would you mind to file a pull request with the updated instructions? :-)

beniroquai, 2022-12-06:
And by the way this looks truely amazing! :)

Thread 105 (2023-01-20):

openUC2/UC2-GIT #105: X-Y Stage Cube

chrisashe00, 2023-01-20:
Hi There

I'm using the same motors you are for assembling  peripheral contolled XY stage. Do you know if there is anywhere on the UC2 platform that has cube designs for this type of motor setup? 

Many Thanks.

beniroquai, 2023-01-22:
Hey @chrisashe00 thanks for reaching out. We have the CAD files available (if you'Re talking about the microsteppers). What exactly are you planning to do? PErhaps I can help.

chrisashe00, 2023-01-24:
Hey! W're planning on building a multi-fluourescence set up and using a peripheral (PS3) controller to control the XY stage. We were actually hoping to see if we could contribute to the Repo also but right now we just wanted to see where we could find a cube for mounting XY stage before we designed one ourselves.

beniroquai, 2023-01-28:
Hey @chrisashe00 sorry for late reply. We do have the STL/CAD for the xy stage. Where exactly do you wanna place the stage? Perhaps I could help you out. 
[00_Chinese_XY-table.stl.zip](https://github.com/openUC2/UC2-GIT/files/10528472/00_Chinese_XY-table.stl.zip)

[image]

chrisashe00, 2023-01-30:
Hey @beniroquai thats cool you have a cad model of the stepper itself!  so we were actually wanting to mount the stepper into a UC2 cube. Hence why we were wondering if a cube existed on the platform that could already hold the microstepper or if we'd have to make one ourselves using CAD software. Any help would be great!

beniroquai, 2023-01-30:
For me, it would be easy to do that. The question is rather how you want to
mount the sample etc.
Would you mind sketching your idea of the cube's insert eventually? This
would help me creating the insert :-)

> Message ID: ***@***.***>
>

chrisashe00, 2023-01-30:
Hi @beniroquai. Here are some sketches I drew of how the stage would sit in the cube (apologies for roughness). Unsure how we are going to mount sample in stage 
[image]
[image]

As for the sample, we have a small rectangle which will hold a slide that should sit on the stage

beniroquai, 2023-01-30:
Thanks for the sketch!
I see. From my personal experience it's be tough to focus through the small
hole of the stage. That's why we used to have two of these stages "back
then":
https://github.com/openUC2/UC2-GIT/tree/master/CAD/ASSEMBLY_XYZ-STAGE_v0

What's your sample geometry and the working distance of your lens?

> Message ID: ***@***.***>
>

chrisashe00, 2023-01-31:
Hey, again thank you for the fast response. 

We are using an infinity lens for our sample, see attached, we're unsure of exact distance but we are using this configuration, so I imagine there will be a few blocks of distance between lens and sample? (See attached skyview diagram)

Infinity Lens: https://www.amazon.ae/ZKAIAI-Professional-Biological-Microscope-Achromatic/dp/B08YXFFLRH

[image]

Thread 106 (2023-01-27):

openUC2/UC2-GIT #106: 45 degrees lens/filter holder

stevenwlee, 2023-01-27:
Hi all,

I require a 3D-printed insert that can securely hold a circular lens like the generic lens holder but at 45 degrees (similar to the 45 degrees mirror holder). This will be specifically for circular dichroic filters.

I've attached a photo of the desired configuration of the dichroic filter cubes, I need to secure (specifically circular) dichroic mirrors at 45 degrees. Please advise me on whether a 3D-printed insert for this has been made before and if there are any STL files for this.

[image]
[image]

Thanks
Steven

beniroquai, 2023-01-28:
Hey Steven, thanks for reaching out. We do have a beamsplitter module for these filters. Perhaps you want to try that one? I attach the STL file here:
[image]

ZIP File:
[20_Cube_Insert_Beamsplittercube_Base_25x25_v3.stl.zip](https://github.com/openUC2/UC2-GIT/files/10528471/20_Cube_Insert_Beamsplittercube_Base_25x25_v3.stl.zip)

stevenwlee, 2023-01-30:
Hi Benedict,

Thanks for your reply, I forgot to mention the diameter of our lenses is 25 mm, to double check, is this suitable? 

Also, the design for the project I'm working on will require the incoming beam to be deflected to the left or right rather than upwards. Thanks very much for sending me the above STL file. I will need some of this insert to be turned 90 degrees so that the filter can be angled similarly to my picture. I need to take the model in your picture and rotate it 90 degrees sideways before changing the sides so it will still lock into a 3dp cube. Does this configuration already exist? 

If not might need to edit this using CAD. And by doing that I might also need a way to tighten the lens on this so it doesn't fall, a bit like the generic lens holder with its removable cover.

Best Regards
Steven

beniroquai, 2023-01-30:
Hey @stevenwlee thanks for your message. I guess I do not fully understand the requirements by your design - sorry ;-) 
Would you mind sketching your idea on paper? I can try designing it in 3D. 
Also, what's the thickness of the lens? (sorry though it's a filter..) Should the lens's center be in the middle of the cube?

stevenwlee, 2023-01-31:
Hi Benedict, thank you very much for your message, The dichroic mirrors I am using all have a thickness of 1 mm (and all have a 25 mm diameter). Please see the drawing of the cube design(shaded) i want to model, and to be clear this it is a sky view perspective.
[image]

I aim to make the incoming light deflected by 90 degrees, but not upwards, but instead right or left. The dashed lines represent where i'd make a hole for line to enter or exit the cube. The dichroic mirror will be angled at 45 degrees, I hope this picture makes it clearer to you. The diagram that my teammate @chrisashe00 also attached in a separate issue also demonstrates how I want to position my dichroic filters (part of our multifluorescence setup). 

[image]

Is there an ipt file for the beam splitter cube you originally sent?

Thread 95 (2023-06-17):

### ISSUE TITLE
Neopixel voltage issues w/ ESP32

### ISSUE THREAD

**Issue by wbrett87** [openUC2/UC2-GIT#95]
I was having issues with using a neopixel array for lighting with an ESP32 (random behaviors like wrong pixels lighting up or wrong colors) here's what I found the solution to be:

The ESP32 outputs 3.2v logic, while the neopixel understands 5v logic. As I understand it, this means that often a 'high' signal (1 in binary) will be interpreted by the neopixel as a 'low'(0 in binary). This leads to unpredictable behavior. My solution was to put a 3.2v to 5v voltage shifter ([available here](https://www.adafruit.com/product/1787?gclid=Cj0KCQjwgO2XBhCaARIsANrW2X0hq6dTdA8NtRoWDUXhl61PgGD2RPxFdzIYT95VlkdHBjJqitz1LSMaAsx_EALw_wcB)) in between my ESP32 and neopixel. In addition I supplied the neopixel array with its own 5v dc power supply, as the ESP32 wasn't providing enough current to light up all of the pixels at once when plugged into a USB.

**Comment by beniroquai** [comment]
Hey, thanks for reporting. Indeed this may causes issues depending on the display you purchase. So far I feel very lucky - not sure why sometimes it works without any issues and sometimes it just doesn't.

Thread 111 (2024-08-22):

openUC2/UC2-GIT #111: Thorslab Tube Lens and Cage System Specifications?

jsmithe2, 2024-08-22:
Hello @beniroquai 

https://github.com/openUC2/UC2-GIT/tree/dea2aca9f7fb344b781abce6a466f22229fd3c4d/CAD/ASSEMBLY_CUBE_Thorlabs

I am trying to make this thorslab cage cube for my Allied Vision Alvium 1800 U-158m. From the information I have here, the cage system is Thorslab CP36 but what would be the proper tube lens for this attachment into the UC2 cube system for this camera?

beniroquai, 2024-08-22:
We use the "ordinary" cage system (e.g. https://www.thorlabs.com/newgrouppage9.cfm?objectgroup_id=4114). This would fit into the cube using this insert. 
As for the tube lens I would rather recommend you to use either a CCTV lens or o 150mm lens depending on the NA you would use and the corresponding sampling criteria on this camera.

jsmithe2, 2024-08-22:
Are you able to provide a link or product number to the types of lenses you are talking about? I understand I will have to adjust based on the NA I decide on.

jsmithe2, 2024-08-23:
@beniroquai More specifically, which tube lens did you use in this picture? Is this a thorslab tube lens?

[image]

beniroquai, 2024-08-30:
Ah, sorry for my late reply. Exactly. This is an achromat from Thorlabs. It could be any, but we used 50,100, 150mm etc. since this is compatible with our standard :)

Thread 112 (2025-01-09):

openUC2/UC2-GIT #112: Baseplate

Grmpfff, 2025-01-09:
Dear UC2 Team,

I would like to print the bigger baseplates that are shown on the pictures to ensure the better stability for towerlike setups (for example the smartphone mikroskope). I regulary saw pictures of the 4x2 and 4x4 baseplate but couldnt find them in the RAW folder or the configurator.
Can anyone provide the stl?
Kind Regards
Benjamin

beniroquai, 2025-01-16:
Hey @Grmpfff sorry for my late reply. A very old version can be found here
https://github.com/openUC2/UC2-GIT/blob/133475f21ddba18bf52d852c6b364a27358937ea/CAD/RAW/STL/Assembly_ALL_PARTS_FOR_EXPORT_10_Base_v0_1.stl
You can arrange them in the slicer software with 50mm spacing so then they will become 1 big baseplate (same for the puzzle pieces by the way). Was this what you needed? 

[image]

Best
Bene

Grmpfff, 2025-01-19:
Thanks very much! I didn't find this folder. I will start looking for the mold cube model there that doesn't need any screws.

beniroquai, 2025-01-19:
Cool! Let us know if you need anything over at https://openuc2.discourse.group/. We hope to create the community there, now :-)

closed 2025-01-19 by beniroquai

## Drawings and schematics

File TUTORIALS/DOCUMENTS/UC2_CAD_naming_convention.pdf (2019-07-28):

# EXTERNAL PARTS

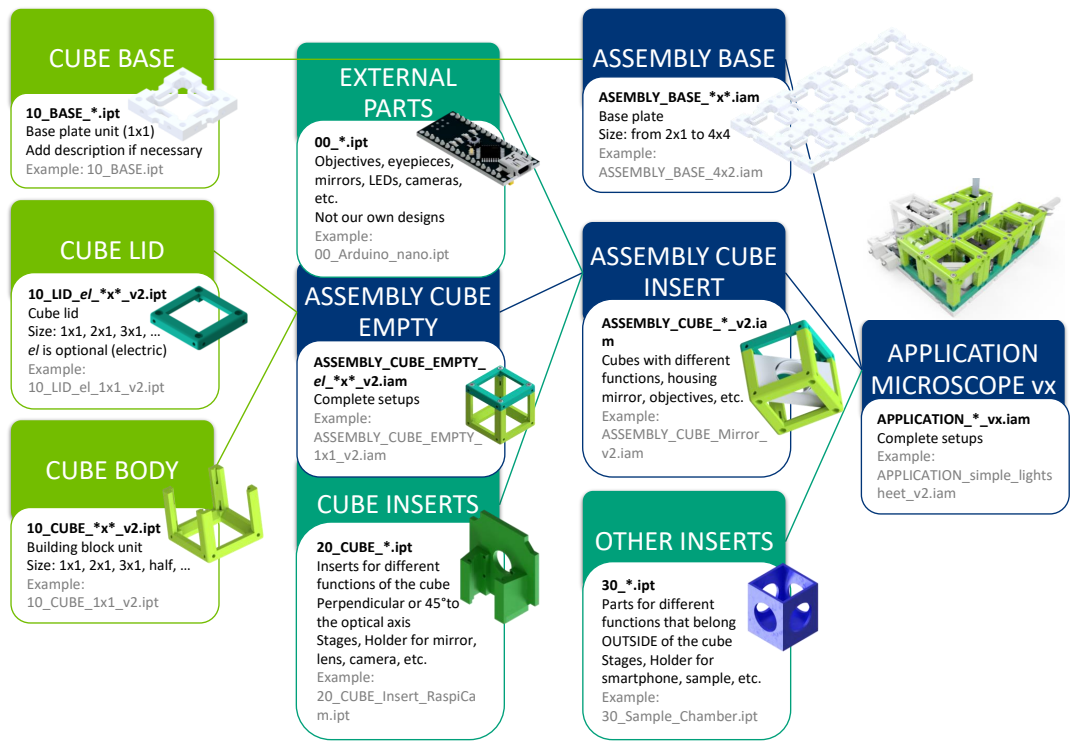
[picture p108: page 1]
APPLICATION MICROSCOPE vx; ASSEMBLY CUBE; CUBE BODY; CUBE LID; CUBE INSERTS; OTHER INSERTS; CUBE BASE; ASSEMBLY BASE; APPLICATION_*; .iam; Complete setups Example: APPLICATION_simple_lights heet_v2.iam; _BASE_*.ipt; ASEMBLY_BASE_*x*; Base plate Size: from 2x1 to 4x4 Example: ASSEMBLY_BASE; 4x2.iam; ASSEMBLY_CUBE_*_v2; m Cubes with different functions, housing mirror, objectives, etc. Example: ASSEMBLY_CUBE_Mirror_ v2.iam; _CUBE_*.ipt; ASSEMBLY_CUBE; _EMPTY_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

Base plate unit (1x1)
Add description if necessary
Example: 10_BASE.ipt

00_*.ipt
Objectives, eyepieces,
mirrors, LEDs, cameras,
etc.
Not our own designs
Example:
00_Arduino_nano.ipt
INSERT ASSEMBLY CUBE
EMPTY

Inserts for different
functions of the cube
Perpendicular or 45
the optical axis
Stages, Holder for mirror,
lens, camera, etc.
20_CUBE_Insert_RaspiCa
m.ipt

30_*.ipt
Parts for different
functions that belong
OUTSIDE of the cube
Stages, Holder for
smartphone, sample, etc.
30_Sample_Chamber.ipt

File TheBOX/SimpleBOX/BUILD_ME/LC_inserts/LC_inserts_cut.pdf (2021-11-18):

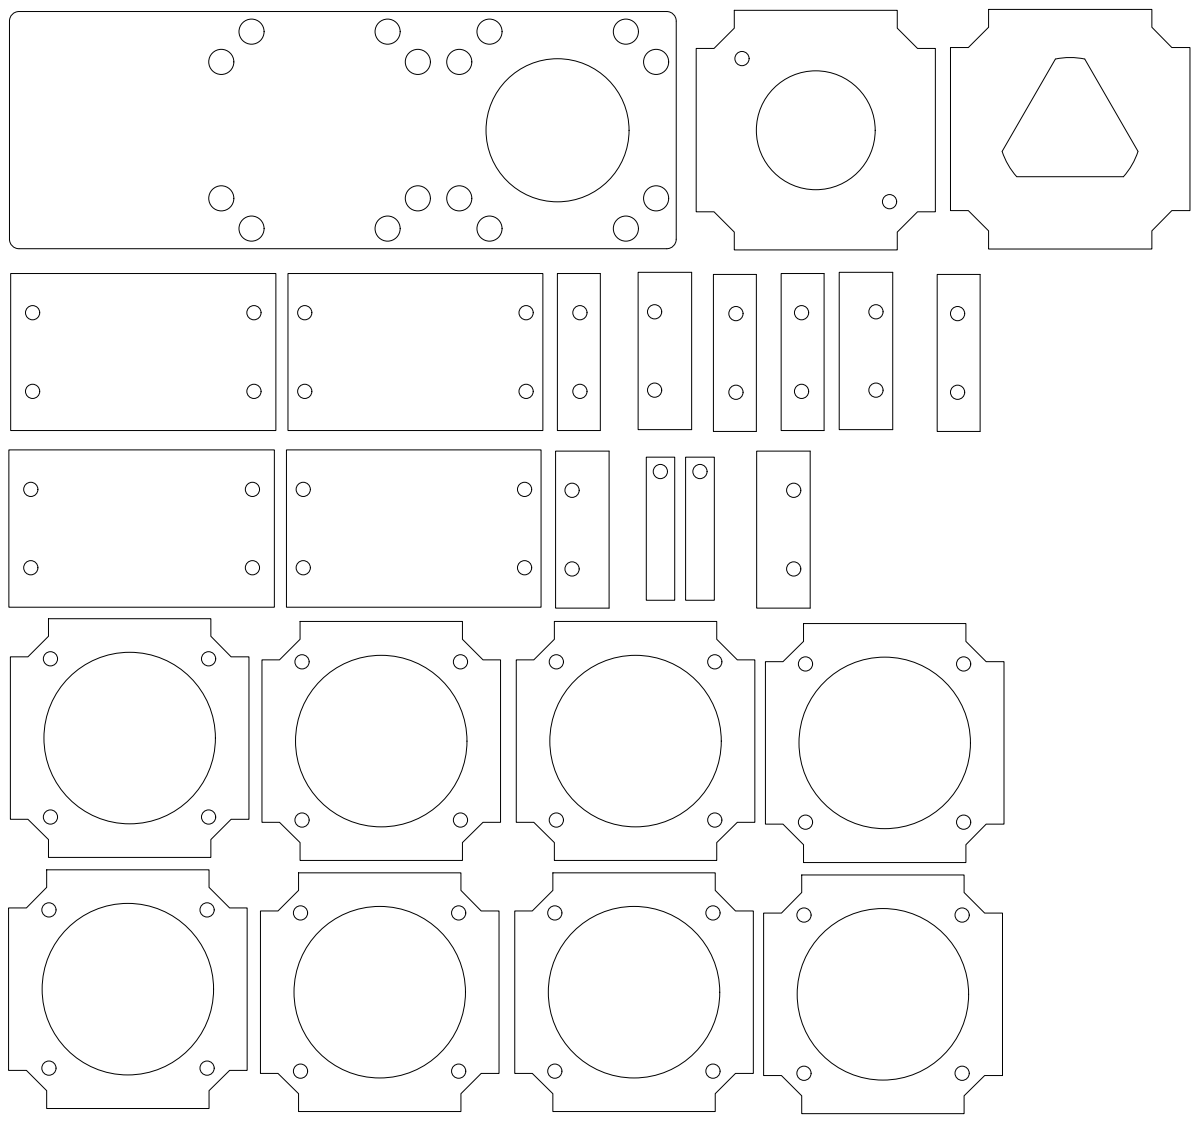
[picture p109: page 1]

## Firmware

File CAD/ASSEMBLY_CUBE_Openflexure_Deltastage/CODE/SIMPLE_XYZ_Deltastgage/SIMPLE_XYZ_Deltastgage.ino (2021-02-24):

// MultiStepper.pde
// -*- mode: C++ -*-
// Use MultiStepper class to manage multiple steppers and make them all move to
// the same position at the same time for linear 2d (or 3d) motion.

#include <AccelStepper.h>
#include <MultiStepper.h>

// create an instance of the stepper class, specifying
// the number of steps of the motor and the pins it's
// attached to
int n_substeps = 1;
  int myspeed = 1000;
  int mynsteps = 800;
int motorPin_X[] = {2,3,4,5};
int motorPin_Y[] = {6,7,8,9};
int motorPin_Z[] = {10,11,12,13};

void setup() {
  Serial.begin(115200);

  // MOTOR
  pinMode(motorPin_X[0], OUTPUT);
  pinMode(motorPin_X[1], OUTPUT);
  pinMode(motorPin_X[2], OUTPUT);
  pinMode(motorPin_X[3], OUTPUT);

    // MOTOR
  pinMode(motorPin_Y[0], OUTPUT);
  pinMode(motorPin_Y[1], OUTPUT);
  pinMode(motorPin_Y[2], OUTPUT);
  pinMode(motorPin_Y[3], OUTPUT);

    // MOTOR
  pinMode(motorPin_Z[0], OUTPUT);
  pinMode(motorPin_Z[1], OUTPUT);
  pinMode(motorPin_Z[2], OUTPUT);
  pinMode(motorPin_Z[3], OUTPUT);
}

void loop() {

  Serial.println("Z+");

  drive_z(mynsteps, myspeed, 1);
  delay(1000);

  Serial.println("Z-");
  drive_z(mynsteps, myspeed, -1);
  delay(1000);

//  Serial.println("X+");
//  drive_x(1000, 1);
//  delay(1000);
//
//  Serial.println("X-");
//  drive_x(1000, -1);
//  delay(1000);
//
//  Serial.println("Y+");
//  drive_y(1000, 1);
//  delay(1000);
//
//  Serial.println("Y-");
//  drive_y(1000, -1);
//  delay(1000);





}


void drive_z(int nsteps, unsigned int motorSpeed, int mydirection) {
int i_iter = nsteps/n_substeps;
  if (mydirection>0){
    for(int i=0; i<i_iter; i++){
    drive_right(motorSpeed, motorPin_X, n_substeps);
    drive_right(motorSpeed, motorPin_Y, n_substeps);
    drive_right(motorSpeed, motorPin_Z, n_substeps);  
    }
  }
  else{
    for(int i=0; i<i_iter; i++){
    drive_left(motorSpeed, motorPin_X, n_substeps);
    drive_left(motorSpeed, motorPin_Y, n_substeps);
    drive_left(motorSpeed, motorPin_Z, n_substeps);  
    }
  }

  stop(motorPin_X);
  stop(motorPin_Y);
  stop(motorPin_Z);
 
}


void drive_right(unsigned int motorSpeed, int motorPin[], int steps)
{ // 1

  int motorPin1 = motorPin[0];
  int motorPin2 = motorPin[1];
  int motorPin3 = motorPin[2];
  int motorPin4 = motorPin[3];

  for (int i = 0; i < steps; i++)
  {
    digitalWrite(motorPin4, HIGH);
    digitalWrite(motorPin3, LOW);
    digitalWrite(motorPin2, LOW);
    digitalWrite(motorPin1, LOW);
    delayMicroseconds(motorSpeed);

    // 2
    digitalWrite(motorPin4, HIGH);
    digitalWrite(motorPin3, HIGH);
    digitalWrite(motorPin2, LOW);
    digitalWrite(motorPin1, LOW);
    delayMicroseconds(motorSpeed);

    // 3
    digitalWrite(motorPin4, LOW);
    digitalWrite(motorPin3, HIGH);
    digitalWrite(motorPin2, LOW);
    digitalWrite(motorPin1, LOW);
    delayMicroseconds(motorSpeed);

    // 4
    digitalWrite(motorPin4, LOW);
    digitalWrite(motorPin3, HIGH);
    digitalWrite(motorPin2, HIGH);
    digitalWrite(motorPin1, LOW);
    delayMicroseconds(motorSpeed);

    // 5
    digitalWrite(motorPin4, LOW);
    digitalWrite(motorPin3, LOW);
    digitalWrite(motorPin2, HIGH);
    digitalWrite(motorPin1, LOW);
    delayMicroseconds(motorSpeed);

    // 6
    digitalWrite(motorPin4, LOW);
    digitalWrite(motorPin3, LOW);
    digitalWrite(motorPin2, HIGH);
    digitalWrite(motorPin1, HIGH);
    delayMicroseconds(motorSpeed);

    // 7
    digitalWrite(motorPin4, LOW);
    digitalWrite(motorPin3, LOW);
    digitalWrite(motorPin2, LOW);
    digitalWrite(motorPin1, HIGH);
    delayMicroseconds(motorSpeed);

    // 8
    digitalWrite(motorPin4, HIGH);
    digitalWrite(motorPin3, LOW);
    digitalWrite(motorPin2, LOW);
    digitalWrite(motorPin1, HIGH);
    delayMicroseconds(motorSpeed);
  }
}

void drive_left(unsigned int motorSpeed, int motorPin[], int steps)
{ // 1

  int motorPin1 = motorPin[0];
  int motorPin2 = motorPin[1];
  int motorPin3 = motorPin[2];
  int motorPin4 = motorPin[3];

  for (int i = 0; i < steps; i++)
  {
    // 1
    digitalWrite(motorPin1, HIGH);
    digitalWrite(motorPin2, LOW);
    digitalWrite(motorPin3, LOW);
    digitalWrite(motorPin4, LOW);
    delayMicroseconds(motorSpeed);

    // 2
    digitalWrite(motorPin1, HIGH);
    digitalWrite(motorPin2, HIGH);
    digitalWrite(motorPin3, LOW);
    digitalWrite(motorPin4, LOW);
    delayMicroseconds(motorSpeed);

    // 3
    digitalWrite(motorPin1, LOW);
    digitalWrite(motorPin2, HIGH);
    digitalWrite(motorPin3, LOW);
    digitalWrite(motorPin4, LOW);
    delayMicroseconds(motorSpeed);

    // 4
    digitalWrite(motorPin1, LOW);
    digitalWrite(motorPin2, HIGH);
    digitalWrite(motorPin3, HIGH);
    digitalWrite(motorPin4, LOW);
    delayMicroseconds(motorSpeed);

    // 5
    digitalWrite(motorPin1, LOW);
    digitalWrite(motorPin2, LOW);
    digitalWrite(motorPin3, HIGH);
    digitalWrite(motorPin4, LOW);
    delayMicroseconds(motorSpeed);

    // 6
    digitalWrite(motorPin1, LOW);
    digitalWrite(motorPin2, LOW);
    digitalWrite(motorPin3, HIGH);
    digitalWrite(motorPin4, HIGH);
    delayMicroseconds(motorSpeed);

    // 7
    digitalWrite(motorPin1, LOW);
    digitalWrite(motorPin2, LOW);
    digitalWrite(motorPin3, LOW);
    digitalWrite(motorPin4, HIGH);
    delayMicroseconds(motorSpeed);

    // 8
    digitalWrite(motorPin1, HIGH);
    digitalWrite(motorPin2, LOW);
    digitalWrite(motorPin3, LOW);
    digitalWrite(motorPin4, HIGH);
    delayMicroseconds(motorSpeed);
  }
}


void stop(int motorPin[])
{
  int motorPin1 = motorPin[0];
  int motorPin2 = motorPin[1];
  int motorPin3 = motorPin[2];
  int motorPin4 = motorPin[3];

  digitalWrite(motorPin4, LOW);
  digitalWrite(motorPin3, LOW);
  digitalWrite(motorPin2, LOW);
  digitalWrite(motorPin1, LOW);
}

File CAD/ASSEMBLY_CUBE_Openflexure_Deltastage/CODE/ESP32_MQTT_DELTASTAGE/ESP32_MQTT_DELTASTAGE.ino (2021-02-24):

/* Here ESP32 will keep 2 roles:
  1/ read data from DHT11/DHT22 sensor
  2/ control led on-off
  So it willpublish temperature topic and scribe topic bulb on/off
*/

#include <WiFi.h>
#include <PubSubClient.h>
#include <AccelStepper.h>
#include <MultiStepper.h>


// EG X-Y position bed driven by 2 steppers
// Alas its not possible to build an array of these with different pins for each :-(
AccelStepper stepper1(AccelStepper::HALF4WIRE, 2, 4, 3, 5);
AccelStepper stepper2(AccelStepper::HALF4WIRE, 6, 8, 7, 9);
AccelStepper stepper3(AccelStepper::HALF4WIRE, 10, 12, 11, 13);

/* change it with your ssid-password */
const char* ssid = "Blynk";
const char* password = "12345678";
/* this is the IP of PC/raspberry where you installed MQTT Server
  on Wins use "ipconfig"
  on Linux use "ifconfig" to get its IP address */
const char* mqtt_server = "192.168.43.88";

/* create an instance of PubSubClient client */
WiFiClient espClient;
PubSubClient client(espClient);

///* topics - DON'T FORGET TO REGISTER THEM! */
#define STEPPER_X_FWD     "stepper/x/fwd"
#define STEPPER_X_BWD     "stepper/x/bwd"
#define STEPPER_Y_FWD     "stepper/y/fwd"
#define STEPPER_Y_BWD     "stepper/y/bwd"
#define STEPPER_Z_FWD     "stepper/z/fwd"
#define STEPPER_Z_BWD     "stepper/z/bwd"

#define CLIENT_ID "ESP32Client_deltastage";


void setup() {

  // Configure each stepper
  stepper1.setMaxSpeed(1000);
  stepper2.setMaxSpeed(1000);
  stepper3.setMaxSpeed(1000);
  // Then give them to MultiStepper to manage
  steppers.addStepper(stepper1);
  steppers.addStepper(stepper2);
  steppers.addStepper(stepper3);

  Serial.begin(115200);
  // We start by connecting to a WiFi network
  Serial.println();
  Serial.print("Connecting to ");
  Serial.println(ssid);

  WiFi.begin(ssid, password);

  while (WiFi.status() != WL_CONNECTED) {
    delay(500);
    Serial.print(".");
  }

  Serial.println("");
  Serial.println("WiFi connected");
  Serial.println("IP address: ");
  Serial.println(WiFi.localIP());

  /* configure the MQTT server with IPaddress and port */
  client.setServer(mqtt_server, 1883);
  /* this receivedCallback function will be invoked
    when client received subscribed topic */
  client.setCallback(receivedCallback);

}

void loop() {
  /* if client was disconnected then try to reconnect again */
  if (!client.connected()) {
    mqttconnect();
  }
  /* this function will listen for incomming
    subscribed topic-process-invoke receivedCallback */
  client.loop();
}




void receivedCallback(char* topic, byte* payload, unsigned int length) {
  Serial.print("Message received: ");
  Serial.println(topic);

  // Convert pointer to int
  int payload_int = 0;
  for (int i = 0; i < length; i++) {
    char c = payload[i];
    if (c >= '0' && c <= '9')
      payload_int = payload_int * 10 + c - '0'; //einzelne Ziffern zu einem Integer zusammenfügen
    else {
      Serial.print ((int)c);
      Serial.println(" war so nicht erwartet");
    }
  }

  Serial.print("Value is : [");
  Serial.print(payload_int);
  Serial.print("]");

  // Catch the value for stepment of lens in X-direction
  if (String(topic) == STEPPER_X_FWD) {
    // Drive motor X in positive direction
    int n_steps_x = (int)payload_int;
    drive_x(n_steps_x, true);
    Serial.print("Motor is running in x for: ");
    Serial.print((int)payload_int);
    Serial.println();
  }

  // Catch the value for stepment of lens in X-direction
  if (String(topic) == STEPPER_X_BWD) {
    // Drive motor X in positive direction
    int n_steps_x = (int)payload_int;
    drive_x(n_steps_x, false);
    Serial.print("Motor is running in x for: ");
    Serial.print((int)payload_int);
    Serial.println();
  }
  // Catch the value for stepment of lens in X-direction
  if (String(topic) == STEPPER_Y_FWD) {
    // Drive motor X in positive direction
    int n_steps_x = (int)payload_int;
    drive_y(n_steps_x, true);
    Serial.print("Motor is running in x for: ");
    Serial.print((int)payload_int);
    Serial.println();
  }

  // Catch the value for stepment of lens in X-direction
  if (String(topic) == STEPPER_Y_BWD) {
    // Drive motor X in positive direction
    int n_steps_x = (int)payload_int;
    drive_y(n_steps_x, false);
    Serial.print("Motor is running in x for: ");
    Serial.print((int)payload_int);
    Serial.println();
  }

  // Catch the value for stepment of lens in X-direction
  if (String(topic) == STEPPER_Z_FWD) {
    // Drive motor X in positive direction
    int n_steps_x = (int)payload_int;
    drive_z(n_steps_x, true);
    Serial.print("Motor is running in x for: ");
    Serial.print((int)payload_int);
    Serial.println();
  }

  // Catch the value for stepment of lens in X-direction
  if (String(topic) == STEPPER_Z_BWD) {
    // Drive motor X in positive direction
    int n_steps_x = (int)payload_int;
    drive_z(n_steps_x, false);
    Serial.print("Motor is running in x for: ");
    Serial.print((int)payload_int);
    Serial.println();
  }
}

void mqttconnect() {
  /* Loop until reconnected */
  while (!client.connected()) {
    Serial.print("MQTT connecting ...");
    /* client ID */
    String clientId = CLIENT_ID;
    /* connect now */
    if (client.connect(clientId.c_str(), "username", "pi")) {
      Serial.println("connected");
      /* subscribe topic with default QoS 0*/
      client.subscribe(STEPPER_Z_BWD);
      client.subscribe(STEPPER_Z_FWD);
      client.subscribe(STEPPER_X_BWD);
      client.subscribe(STEPPER_X_FWD);
      client.subscribe(STEPPER_Y_BWD);
      client.subscribe(STEPPER_Y_FWD);

    } else {
      Serial.print("faiLED_PIN, status code =");
      Serial.print(client.state());
      Serial.println("try again in 5 seconds");
      /* Wait 5 seconds before retrying */
      delay(5000);
    }
  }
}


void drive_x(int nsteps, int mydirection){
  long positions[3]; // Array of desired stepper positions
  positions[0] = mydirection*nsteps;
  positions[1] = mydirectionnsteps;
  positions[2] = -nsteps;
  steppers.moveTo(positions);
  steppers.runSpeedToPosition(); // Blocks until all are in position 
}

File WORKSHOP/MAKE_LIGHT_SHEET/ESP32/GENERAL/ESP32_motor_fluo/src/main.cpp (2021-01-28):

// ----------- ----------- ----------- ----------- ----------- -----------
// ESP32 script to accept MQTT commands for UC2-control
// by: Rene Lachmann
// date: 11.09.2019
// based on Arduino-Interface by Rene Lachmann, Xavier Uwurukundu
//----------- ----------- ----------- ----------- ----------- -----------

// ----------------------------------------------------------------------------------------------------------------
//                          INCLUDES
#include <WiFi.h>
#include <PubSubClient.h>
#include <string.h>
#include <vector>
#include <StepMotor.h>
#include "driver/ledc.h"
#include <ctime>
#include <sstream>
// ----------------------------------------------------------------------------------------------------------------
//                          Global Defines
#define MAX_CMD 3
#define MAX_INST 10
#define NCOMMANDS 15
#define MAX_MSG_LEN 40
#define LED_BUILTIN 11
#define LED_FLUO_PIN 26

// ----------------------------------------------------------------------------------------------------------------
//                          Parameters
// ~~~~ Device ~~~~
// create Pseudo-random number with temporal dependent input

// saved in strings, so that later (if implemented) e.g. easily changeable via Bluetooth -> to avoid connection errors
std::string SETUP = "S013";      //S006->Aurelie; S004->Barbora
std::string COMPONENT = "MOT01"; // LAR01 //LED01 // MOT02=x,y // MOT01=z
std::string DEVICE = "ESP32";
std::string DEVICENAME;
std::string CLIENTNAME;
std::string SETUP_INFO;

// ~~~~  Wifi  ~~~~
const char *ssid = "UC2_wifi004";
const char *password = "_lachmannUC2";
WiFiClient espClient;
PubSubClient client(espClient);
// ~~~~  MQTT  ~~~~
const char *MQTT_SERVER = "21.3.2.152";
const int MQTT_PORT = 1883;
const char *MQTT_CLIENTID;
const char *MQTT_USER;
const char *MQTT_PASS = "23SPE";
const int MQTT_SUBS_QOS = 0;
//const int MAX_CONN = 10; // maximum tries to connect
const unsigned long period = 80000; // 80s
unsigned long time_now = 0;
// topics to listen to
std::string stopicREC = "/" + SETUP + "/" + COMPONENT + "/RECM";
std::string stopicSTATUS = "/" + SETUP + "/" + COMPONENT + "/STAT";
std::string stopicANNOUNCE = "/" + SETUP + "/" + COMPONENT + "/ANNO";
// Deliminators for CMDs (published via payload-string)
const char *delim_inst = "+";
const int delim_len = 1;

// ~~~~ MOTOR ~~~~
StepMotor stepperZ = StepMotor(25,26,27,14); //normally: 25, 26, 27, 14 // 12, 14, 27, 26
StepMotor stepperY = StepMotor(5, 17, 16, 4);
StepMotor stepperX = StepMotor(33, 32, 27, 14); // 27, 25, 32, 4 never connected to same ESP32 as stepperZ -> hence: universally possible

// ~~~~ FLUO ~~~~
int led_fluo_pwm_frequency = 12000;
int led_fluo_pwm_channel = 0;
int led_fluo_pwm_resolution = 8;

// ~~~~ Commands ~~~~
const char *CMD;     //Commands like: PXL -> limited to size of 3?
int *INST[MAX_INST]; //Maximum number of possible instructions =
std::vector<int> INSTS;
std::string CMDS;

const char *COMMANDSET[NCOMMANDS] = {"DRVX", "DRVY", "DRVZ", "FLUO"};
const char *INSTRUCTS[NCOMMANDS] = {"1", "1", "1", "1"};
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

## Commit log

2018-08-18 Initialized Folder Structure
    [Bill_of_Materials_Fluidscope_v0.xlsx]
2018-08-19 Inline Holographical System published
    + Electronics
    + Bill of material
    + other stuff
    [INLINE_HOLOGRAM_00_Base_4x4_v0.stl, INLINE_HOLOGRAM_00_Ray_INLINE_17.stl, INLINE_HOLOGRAM_00_Sample_Slide_16.stl, INLINE_HOLOGRAM_10_Cube_v0_6.stl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]
2018-08-19 Added Incubator Microscope
    [IN-INCUBATOR_MICROSCOPE_v0_00_Base_v0_1.stl, IN-INCUBATOR_MICROSCOPE_v0_00_Base_v0_2.stl, IN-INCUBATOR_MICROSCOPE_v0_00_Base_v0_3.stl, IN-INCUBATOR_MICROSCOPE_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]
2018-08-22 Added Bill-of-material and Docu
    [00_BallMagnets_6mm.ipt, 00_Base_v0.ipt, 10_Cube_v0.ipt, 10_Lid_el_v0.ipt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]
2018-08-22 Changed folder structure, added README
    [IN-INCUBATOR_MICROSCOPE_v0_00_Base_v0_1.stl, IN-INCUBATOR_MICROSCOPE_v0_00_Base_v0_2.stl, IN-INCUBATOR_MICROSCOPE_v0_00_Base_v0_3.stl, IN-INCUBATOR_MICROSCOPE_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]
2018-08-22 Minor changes
    [Bill_of_Materials_In-Incubator-Microscope_v0.xlsx]
2018-08-31 Added Documentation, Cleanup
    [Assembly_Lightsheet_Laserscanner_v0_00_Base_1x3_v0_00_Base_v0.stl, Assembly_Lightsheet_Laserscanner_v0_00_Microscope_Objective_Lens10x_83.stl, Assembly_Lightsh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]
2018-10-02 Initial commit for workshop guide.
    [XY_Stage_v0.fzz]
2018-10-04 Updated Workshop section
    [INLINE_HOLOGRAM_00_Base_4x1_v0.stl, INLINE_HOLOGRAM_00_Ray_INLINE_17.stl, INLINE_HOLOGRAM_00_Sample_Slide_16.stl, INLINE_HOLOGRAM_10_Cube_v0.stl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]
2018-10-04 Updated the documentation for Electronics
    [LED_Matrix_v0.fzz, XY_Stage_v0.fzz]
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2018-10-08 Added Electronic Mounts
    [Assembly_Electronics_70_Electronics_Baseplate_1.stl, Assembly_Electronics_70_Electronics_ESP32_2.stl, Assembly_Electronics_70_Electronics_Mount_Arduino_3.stl]
2018-10-09 Added simple Telescope to CAD files
    [Assembly_simple_Telescope_00_50mm_Rod_Thorlabs.stl, Assembly_simple_Telescope_CP02_M-Step.stl, INLINE_HOLOGRAM_00_Base_4x1_v0.stl, INLINE_HOLOGRAM_10_Cube_v0.s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]
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2018-11-19 Updated Docu Electronics
    [LED_Matrix_v0.fzz]
2018-11-22 Updated the documentation
    Added a link section for parts and knowledge. Reorganized the Documents.
    [Bill_of_Materials_In-Incubator-Microscope_v0.xlsx]
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2018-12-05 Added the XYZ-Stage Files including the Tutorial
    [Assembly_XYZ_Stage_00_Base_v0_14.stl, Assembly_XYZ_Stage_00_large_gear_6.stl, Assembly_XYZ_Stage_00_small_gear_7.stl, Assembly_XYZ_Stage_05__RMS_Adapter_v2_5.s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]
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2019-03-20 Added the Telescope Workshop.
    [Assembly_Custom_Lens_Adapter_11_Lens_Thorlabs_Mount_Customized_B_1.stl, Assembly_Custom_Lens_Adapter_11_Lens_Thorlabs_Mount_Ring_B_2.stl]
2019-04-08 Included Designfiles and Tutorial for the base cube
    [00_BallMagnets_6mm.ipt, 00_Base_v0.ipt, 10_Cube_v0.ipt, 10_Lid_el_v0.ipt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]
2019-04-08 Added descritpion for usage in Inventor/Fusion
    [Mold Design.iam, Weldment (ANSI - mm).iam]
2019-04-08 Added 3D printing instructions
    [BASE_CUBE_v0_00_BallMagnets_6mm_4.stl, BASE_CUBE_v0_DIN 912 - M3 x 0.5 x 12 x 10.75_5.stl, BASE_CUBE_v0_DIN 912 - M3 x 0.5 x 12 x 10.75_6.stl, BASE_CUBE_v0_DIN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]
2019-05-10 Generated figure for publication
    -HeLa cell to compare with the Q-PHase result
    [Z_Stage_ESP_v0.fzz]
2019-05-12 Updated the entire documentaiton.
    - New tutorials for each part are now available
    [10_Cube_v0_B.ipt, 10_Cube_v0_f-50.stl, 10_Cube_v0_f100.stl, 10_Cube_v0_f50.stl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]
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2019-05-12 Renaming and adding the Filter Cube
    [10_Cube_v0.ipt, 10_Lid_el_v0.ipt, Assembly_Cube_Beamsplitter_10_Cube_v0_3.stl, Assembly_Cube_Beamsplitter_10_Lid_el_v0_2.stl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]
2019-05-13 Added code for the XY-Stage
    [Assembly_Cube_cameracube_10_Cube_v0_4.stl, Assembly_Cube_cameracube_10_Lid_el_v0_3.stl, Assembly_Cube_cameracube_11_Mirror_Adapter_for_RaspiCam_2.stl]
2019-05-14 Added the optical alignment section of the lightsheet workshop
    [Assembly_XY_Translator_Lightsheet_v2_00_Syringe_holder_lid_3.stl, Assembly_XY_Translator_Lightsheet_v2_00_X_Translator_Lightsheet_v4_4.stl, Assembly_XY_Transla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]
2019-05-15 Typo and Cleanup
    [10_Cube_v0_B.ipt, 10_Cube_v0_f-50.stl, 10_Cube_v0_f100.stl, 10_Cube_v0_f50.stl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]
2019-05-16 Some Refactoring and adding of the new telescope file.
    [01_pretty_telescope_iphone_20mm.stl, Assembly_Cube_prettytelescope_01_pretty_telescope_iphone_12_20mmlens.stl, Z_Stage_ESP_v0.fzz]
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2019-07-03 Updated Files for the Inline Holographic Microscope
    [50_Cube_Insert_Thorlabs.stl, BASE_CUBE_v2_00_BallMagnets_6mm_2.stl, BASE_CUBE_v2_00_Base_v0_1.stl, BASE_CUBE_v2_10_Cube_Base_4.stl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]
2019-07-03 Added some files for the Holographic Documentation Thing
    [INLINE_HOLOGRAM_00_Reflector.stl, INLINE_HOLOGRAM_11_Mirror_Adapter_for_RaspiCam.stl]
2019-07-04 Many updates to the Documentaton of the Inline Holographical microscope
    [INLINE_HOLOGRAM_00_Reflector.stl, INLINE_HOLOGRAM_10_Inlet_LED_Reflector.stl]
2019-07-04 Added new Incubator microscope
    [Assembly_UKJ_Microscope_Assembly_base_4x2.stl, Assembly_UKJ_Microscope_v4_00_focus_inlet_triangle_spiral_v6.stl, Assembly_UKJ_Microscope_v4_01_28BYJ_Coupling_S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]
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2019-07-11 Updated to new IMJOY and Floumodule
    [Assembly_Cube_2x1_Z-Stage_Sampleholder_00_FluidicChip_AlexSwen_2.stl, Assembly_Cube_2x1_Z-Stage_Sampleholder_40_XY_Stage_Chipclamp_1.stl, Assembly_Cube_2x1_Z-S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]
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2019-07-17 Added the Smartphone Microscope to the applications.
    [Assembly_smartphone_microscope_00_focus_inlet_triangle_spiral_v6_40.stl, Assembly_smartphone_microscope_01_28BYJ_Coupling_ScrewM4_19.stl, Assembly_smartphone_m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]
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2019-07-25 Base cube in openscad v0 (alpha)
    [bla.scad]
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2019-07-26 Corrected lengths
    [bla.scad]
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2019-09-27 STL folders updated, broken links fixed
    [10_Cube_1x1_v2.stl, 10_Cube_2x1_v2.stl, 10_Cube_2x1_v2_7.stl, 10_Lid_1x1_el_v2.stl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]
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2020-01-28 Added fixed les holder
    [07_20_focus_inlet_plate.stl, 1inch_Assembly_Insert_Lens_mount_fixed_20_Lens_holder.stl, 1inch_Assembly_Insert_Lens_mount_fixed_20_Lens_holder_clamp.stl, 20_Len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]
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2020-03-31 Fixed errors and broken links in previous update
    [01_10_Cube_2x1_v2.stl, 02_10_Lid_el_2x1_v2.stl, 03_10_Cube_1x1_v2.stl, 04_10_Lid_1x1_v2.stl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]
2020-04-02 Main: added draw.io libraries into MDK
    Fixed errors in previous pushes
    Improved CAD readme
    Updated fullBOX simple schemes
    [00_BallMagnets_5mm.ipt, 10_Base_v0.ipt, 10_Cube_1x1_v2.ipt, 10_Lid_1x1_v2.ipt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]
2020-04-03 Main: CAD folder brushed up
    Added Eyeball cube
    Added text to TheBOXes
    Fixed many typos in CAD folders
    Kinematic mirror do not need metal plates now
    Sample holder for thicker slides
    All baseplates have correct orientation for printing
    [05_Assembly_base_4x1.stl, 10_Cube_1x1_v2.stl, 10_Lid_1x1_v2.stl, 16_20_Cube_insert_Sample_holder.stl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]
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2020-05-04 Solved issue #25
    [05_Assembly_base_4x1.stl, 10_Base_v2.stl, Assembly_base_4x1.stl]
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2020-05-13 Fixed many broken links
    Added INVENTOR folder to the CAD\ASSEMBLY_CUBE_Mirror_45_v2 with original design files and linked it in the respective readme - all the folders in CAD should have this soon
    Updated some resources
    [10_Cube_1x1_v2.ipt, 10_Lid_1x1_v2.ipt, 20_Cube_Insert_Mirror_Holder_v2.ipt, ANSI (in).dwg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]
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2020-05-22 Fixed errors in previous update
    [Cube_Lid_1x1_v2.scad, UC2_Cube_Lid_1x1_v2.scad, UC2_Insert_Perpendicular.scad, UC2_Lens_insert_v2.scad]
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2020-06-17 Fixed error in openSCAD Lens holder file
    [UC2_Lens_insert_v2.scad, UC2_lens_insert_d25,4_t1,5.stl]
2020-06-29 Adding the infinity-corrected fluorescence microscope.
    [10_Cube_1x1_v2.stl, 10_Cube_2x1_v2.stl, 10_Lid_1x1_v2.stl, 10_Lid_el_2x1_v2.stl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]
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2020-08-03 Fixed many broken links
    [UC2_Lens_insert_v2_-50mm.stl, UC2_Lens_insert_v2_100mm.stl, UC2_Lens_insert_v2_40mm.stl]
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2021-01-11 CAD - most issues fixed
    [10_Cube_2x1_v2.stl, 10_Lid_el_2x1_v2.stl, 20_Insert_Large_Lens_holder_v3.scad, 20_Insert_Lens_holder_v3.scad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]
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2021-01-19 Updates: BOXes, modules
    Z-stage objective added to configurator excel sheet
    excel sheet corrected for BOXes
    updated BOXes build_me
    updated tutorials:
    kinematic mirror
    [UC2_ReadyToUse_Boxes_Modules_Parts.xlsx]
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2021-01-21 Fixed random issues
    replaced some old images
    broken links
    not for buying the cubes
    smartphone holder added for miniBOX
    [UC2_ReadyToUse_Boxes_Modules_Parts.xlsx]
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2021-02-05 Fixing error with delta stage in configurator; Cleanin up with OFM stuff.
    [20_Cube_Insert_Openflexure_Adapter Kopie.stl, 20_Cube_Insert_Openflexure_Adapter.stl, 20_Cube_Insert_Openflexure_Deltastage_Adapter.ipt, 20_Cube_Insert_Openfle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]
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2021-03-19 Revert "updates"
    This reverts commit 9abd0d05d86b170f751e089448e35b0d46d5e5db.
    [00_Laser_Clamp_OnOffSwitch.stl, 10_Cube_1x1_v2.stl, 10_Cube_sample_chamber.stl, 10_Cube_sample_chamber_x2_50mm.stl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]
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2022-11-17 Corrections on PolarBOX and BOXes
    [00_Laser_Clamp_OnOffSwitch.ipt, 00_Laser_Clamp_OnOffSwitch.stl, 10_Cube_1x1_v2.ipt, 10_Cube_1x1_v2.stl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]
2022-11-17 Fixing broken links - part1
    [Assembly_Cube_Baseplate_4x1_v2.stl, Assembly_Cube_Baseplate_4x4_v2.stl]

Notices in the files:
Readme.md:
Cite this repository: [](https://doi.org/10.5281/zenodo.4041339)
